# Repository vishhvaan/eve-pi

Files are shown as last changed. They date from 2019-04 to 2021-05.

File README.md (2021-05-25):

The EVoltionary biorEactor

The EVE is an open framework for an automated continuous culture system.

  - Easy to use for programmers and non-programmers
  - Cheap
  - Replicate functionality of a morbidostat/chemostat/turbidostat
  - Versatile & easily modifiable for different purposes

This device is meant to be used for the study of population dynamics and evolution.

# Build it!
Head over to [Start Building] folder to find the 3D stls and circuit schematics (along with KiCAD project). 

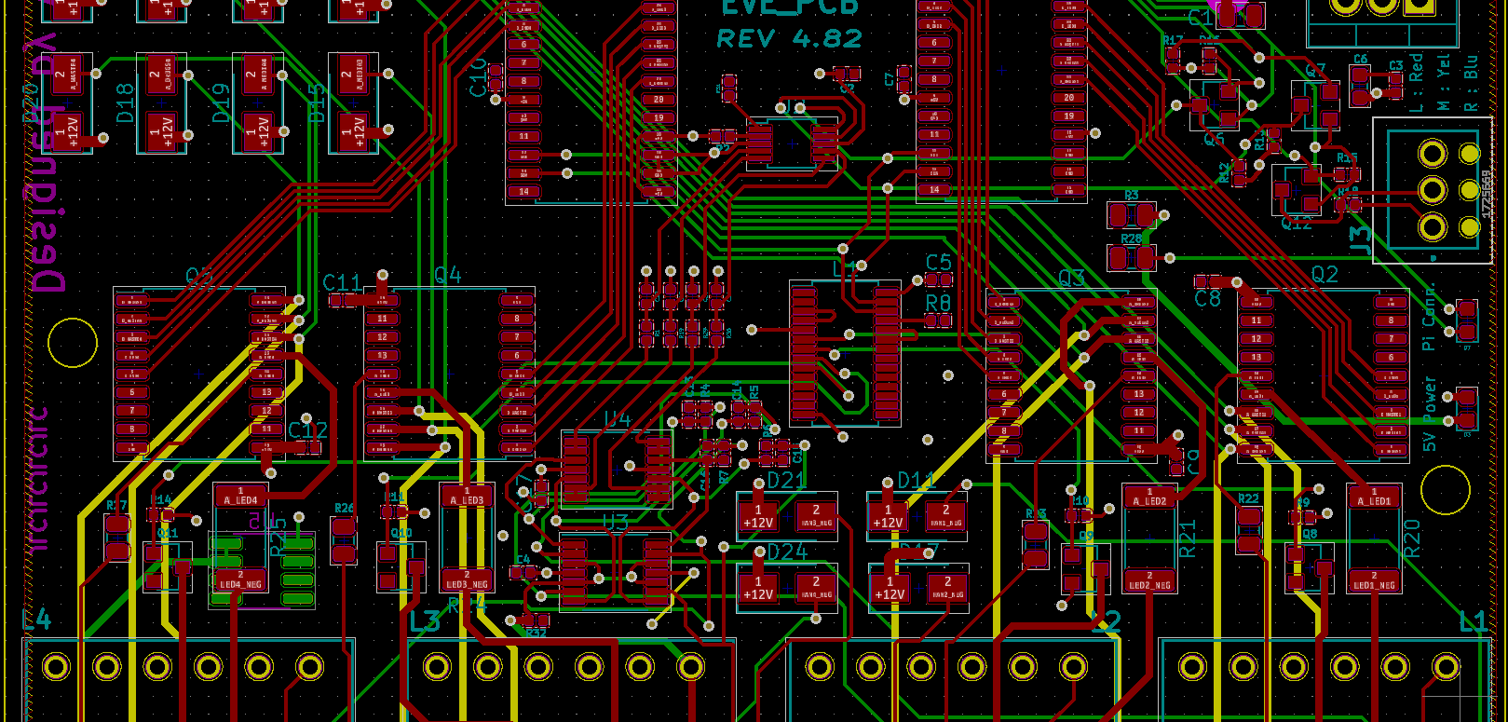
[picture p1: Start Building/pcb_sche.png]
PCB


<p align="center">
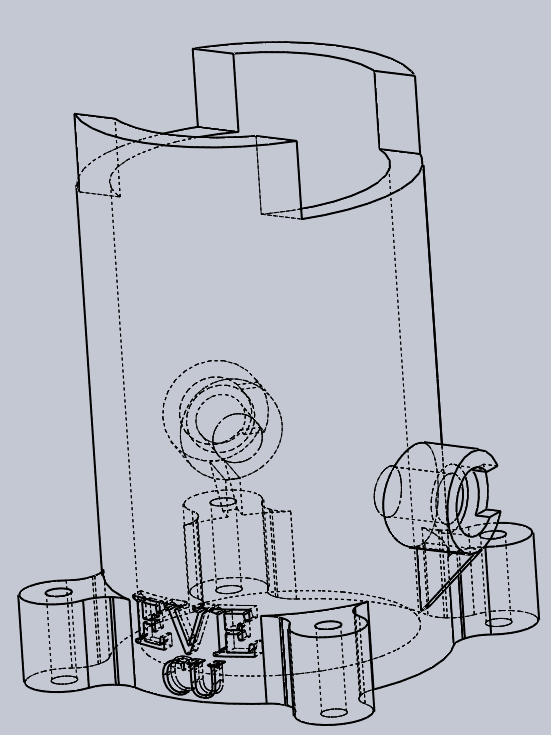
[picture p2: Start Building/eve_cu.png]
  
</p>

# Installation

1. Download and flash the [Raspbian] Buster OS on an SD card.
2. Insert the SD Card into the Pi and connect the Pi to a display, keyboard, local area network, and power.
3. Note the IP address of the device with the command:
```sh
$ ifconfig
```
4. Enter super user mode with the command:
```sh
$ sudo su
```  
5. Run the setup script by entering the command: 
```sh
$ bash <(curl -s https://raw.githubusercontent.com/vishhvaan/eve-pi/master/st_eve.sh)
```
6. Follow the on-screen instructions to install the software.
7. Navigate to the folder `scripts/live/` and copy the `sample-conf.in` to `eve-conf.ini`.
8. Edit the `eve-conf.ini` file based on the "Configuration File Parameter Definitions" file in the "Start Building" folder.\*
9. If the Pi has a browser, navigate to the web interface by accessing: http://localhost.
10. On a browser on the network, navigate to the web interface by accessing the IP address or hostname of the device (e.g. http://eve.local_domain.net).

\* If the PCB is used or the breadboard was wired like the schematic, the default values for the hardware address in the sample-conf.ini file will work.

For a headless install:

1. Download and flash the [Raspbian] Buster OS on an SD card.
2. Add a file titled `ssh` to the boot partition.
3. Insert the SD Card into the Pi and connect the Pi to the local area network and power.
4. In a seperate computer's terminal run a command to connect to the pi.
```sh
$ ssh pi@raspberrypi
```  
5. Login to the pi with the password `raspberry`
6. Continue from step 3 in the non-headless install.

## Install for Docker for ARM Devices
 
Pre-built images coming soon to Docker Hub!

### Build the Docker Image

Use the Dockerfiles in the repo to build images yourself. Use the images to spin up containers in the Pi with EVE WebUI and all the programs built-in.

#### On ARM Devices

1. [Install Docker] on the Raspberry Pi.
2. Install git on the Raspberry Pi.
```sh
$ sudo apt install -y git
```  
2. Clone the repository to the home directory.
```sh
$ sudo git clone https://github.com/vishhvaan/eve-pi.git /eve
```  
3. Move to the correct directory.
```sh
$ cd /eve
``` 
4. Run the Docker build command.
```sh
$ docker build -t eve:pi .
```  
5. Create a container.
```sh
$ docker create --name = eve1 \
    -p 80:80 \
    -p 8050:8050 \
    -e PUID=1000 \
    -e PGID=1000 \
    -v /eve/data:/data \
    eve:pi
```  
6. Start the container.
```sh
$ docker start eve1
```  

#### On UNIX-based x86/x64 Devices
Emulate the ARM environment with QEMU. Build images with the Dockerfile.arm32v7.

### Shout Outs
The EVE uses a number of open source projects to work properly:

  - [script-server] -  Script server to run programs on the Pi
  - [slack-api] - Uses the Slack API for Python for experiment monitoring
  - [plotly] - Uses Dash for real-time plotting
  - [KiCAD] - For Circuit Schematics and PCB Designs
  - [Docker] - For creating self-contained application platforms

## New Features
 
  - Configurable save locations (USB or Network)
  - Combined graphs of culture units

<!--![GitHub All Releases](https://img.shields.io/github/downloads/vishhvaan/eve-pi/total)-->

License
----

MIT

   [script-server]: <https://github.com/bugy/script-server>
   [slack-api]: <https://github.com/slackapi/python-slackclient>
   [Start Building]: <https://github.com/vishhvaan/eve-pi/tree/master/Start%20Building>
   [plotly]: <https://plot.ly/dash/>
   [KiCad]: <http://www.kicad-pcb.org/>
   [Install Docker]: <https://github.com/docker/docker-install>
   [Raspbian]: <https://www.raspberrypi.org/downloads/raspbian/>
   [Docker]: <https://github.com/docker/docker-ce>

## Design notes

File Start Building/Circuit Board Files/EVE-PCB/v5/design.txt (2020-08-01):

3 CU

Daisy Chainable

CU1 = 2 LED/ 2 PD / 4 Pumps
CU1 = 1 LED/ 1 PD / 4 Pumps
CU1 = 1 LED/ 1 PD / 4 Pumps

TCA9548A for sda/scl
- Address select via solder pads
- 8 breakouts

2x PWM PCA9685 
- 16 channels
- 1 x (4pumps, 2LED, 2IND) = 8 channels
- 2 x (4pumps, 1LED, 1IND) = 6 channels
20 channels total

1x ADS1115
- 4 channels
- With op amp for photopdiode

2x AD5241
- 1mohm
- with 1quad opamp
- for inital amp

- op amp with hardwired amp and low pass filter (?)
- amp 5/4
- diode protection for op amp

1x AD5254
- Quad pot
- 10 k
- 5V power + Vab
- CU LED R

1x I2C VRef for OD signals
- Voltage limiting circuit

- high current output voltage follower
- 2x ALM2402-Q1
- (more expensive) 4x OPA564
- 2ohm 1W resistor

Change shotkey to PMEG6010CEH

Logic level inverter for PWM (SN74LVC1G04)
Logic level shifter for SDA/SCL (?)

Integrate Temp Sensor

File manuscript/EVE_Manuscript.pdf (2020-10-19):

Manuscript submitted to eLife
1 | A Low-Cost, Open Source,
2 | Self-Contained Bacterial
3 | EVolutionary biorEactor (EVE)

Vishhvaan Gopalakrishnan¹

, Nikhil P. Krishnan²

, Erin McClure³,†
, Julia Pelesko⁴
4 | ,
Dena Crozier¹,2, Kyle J. Card³

, Drew F.K. Williamson³,‡
, Nathan Webster³
5 | , Daniel
Nichol⁵

, Soumyajit Mandal⁶
, Robert A. Bonomo⁷

, Jacob G. Scott³,4,8,9
6

*For correspondence:
vxg135@case.edu (VG);
scottj10@ccf.org (JGS)

Present address: †University of South Florida Morsani School of Medicine, Tampa, Florida, United States of America; ‡Current Address: Department of Pathology, Brigham and Women’s Hospital, Boston, Massachusetts, United States of America

1
7 | Lerner College of Medicine, Cleveland Clinic, Cleveland, Ohio, United States of America;
| 2
8 | Case Western Reserve University School of Medicine, Cleveland, Ohio, United States of
America; 9
| 3Department of Translational Hematology and Oncology Research, Cleveland
Clinic, Cleveland, Ohio, United States of America; 10
| 4Department of Physics, Case Western
| Reserve University, Cleveland, Ohio, United States of America ; 5
11 | Centre for Evolution
| and Cancer, The Institute of Cancer Research, London, United Kingdom; 6
12 | Integrated
13 | Circuits and Sensor Physics Lab, Case Western Reserve University School of Engineering,
Cleveland, Ohio, United States of America; 14
| 7Department of Medicine, Louis Stokes
15 | Cleveland Department of Veteran Affairs Medical Center, Cleveland, Ohio, United States
of America; 16
| 8Department of Radiation Oncology, Cleveland Clinic, Cleveland, Ohio,
| United States of America; 9
17 | Center for Proteomics and Bioinformatics, Case Western
18 | Reserve University School of Medicine, Cleveland, Ohio, United States of America;
| +
19 | Current Address: University of South Florida Morsani School of Medicine, Tampa,
| Florida, United States of America; 1
20 | Current Address: Department of Pathology, Brigham
21 | and Women’s Hospital, Boston, Massachusetts, United States of America

22

23 | Abstract Evolutionary forces shape bacterial population characteristics in a matter of days.
24 | Here, we present a framework that allows students and scientists to study bacterial evolution of
25 | antibiotic resistance over a few days. This approach is in line with recent efforts to study
26 | evolution of drug resistance in organisms at increasingly smaller time scales and in a
27 | high-throughput manner. One effective approach is through the use of customized bioreactors –
28 | devices that can continuously culture bacteria and monitor population growth in real time. These
29 | devices are often technically challenging and expensive to implement for scientists, let alone
30 | students or teachers who seek an innovative and intuitive way of studying evolution. Here, we
31 | present a continuous bacterial culture device that can be easily and inexpensively constructed,
32 | flexibly configured for various evolution experiments, and used in both academic and
33 | educational environments. As this EVolutionary biorEactor (EVE) is capable of replicating the
34 | functionality of many prominent and expensive bioreactors on the market today, we hope the
35 | greater accessibility of EVE will allow interested high school and college students to study
36 | biological concepts such as population dynamics and evolution using innovative technology.
37 | Within the educational environment, we also hope to foster interaction and interest between the
38 | engineering and biological fields by allowing teachers and students to build their own systems
39 | and share experimental designs and results based on our proposed open framework.

40

41 | Introduction
42 | Continuous microbial culture is a powerful, high-throughput method of observing and directing
43 | evolution in both research and industrial settings. Bioreactors are continuous culture devices that
44 | simultaneously passage media into and remove volume from active cultures to maintain volume
45 | homeostasis Novick and Szilard (1950). The rate of media inflow and outflow is called the dilution
46 | rate; various types of bioreactors dynamically adjust the dilution rate to keep a desired parameter
47 | constant. Chemostats, the simplest bioreactors, maintain a constant dilution rate Voulgarelis et al.
48 | (2019). Turbidostats adjust the dilution rate to maintain a constant turbidity. Finally, auxostats refer
49 | to bioreactors that use any other parameter to control the dilution rate. Examples of parameters
50 | used in auxostats include pH and oxygen tension.
51 | Here, we present a protocol for the assembly and operation of a continuous culture device
52 | called the the EVolutionary biorEactor (EVE). It is a framework for a system which can support mul-
53 | tiple individual bioreactors, which we call culture units (CUs). Each of these CUs are capable of
54 | simultaneously running their own experiment with different antibiotics, rates of passaging media
55 | and removing waste, population density sampling rates, and many other customizable parame-
56 | ters. The EVE system began by openly and cost-conservatively replicating and expanding upon the
57 | morbidostat functionality using the methodology outlined by Toprak et al.. The morbidostat keeps
58 | the cell density low by exposing the population to selective pressures such as cytotoxic drugs. To
59 | prevent extinction of the culture, the morbidostat control algorithm temporally modifies the con-
60 | centration of drug delivered to the in accordance to the adaptive dynamics of the population under
61 | study. Toprak et al. (2013).
62 | The physical functionality of the EVE is centered around a culture vial and is inspired by promi-
63 | nent bioreactors featured in the literature Toprak et al. (2013); Yoshida et al. (2017); Wong et al.
64 | (2018); Milias-Argeitis et al. (2016); Dößelmann et al. (2017). Traditionally, costs of commercially-
65 | available bioreactors range from approximately $10,000 for academic units to $25,000 for the gen-
66 | eral public. These bioreactors are often built specifically for one field of research and are difficult
67 | to modify for other applications. However, a recent shift towards open-source science has brought
68 | about a new wave of do-it-yourself, customized continuous culture devices to accommodate a wide
69 | variety of experimental designs across several research areas Nash (2005); Matteau et al. (2015);
70 | Gill (2018); Cressey (2017); Perkel (2017); Pilizota and Yang (2018). At the same time, the prolif-
71 | eration of maker-spaces throughout high schools and colleges have increased student access to
72 | engineering and design resources. As a result, bioreactors are an ideal educational tool to foster
73 | interest in experimental evolution for college, high school, and even elementary school students.
74 | A few such designs with detailed protocols have already been published in the literature. How-
75 | ever, barriers in electrical, software, and biological expertise, as well as cost, still leave the assembly
76 | and operation of these machines out of reach for students or scientists in resource-poor settings
77 | Yoshida et al. (2017); Toprak et al. (2013); Wong et al. (2018). In addition, increasing the function-
78 | ality of these machines while maintaining cost-effectiveness is an enduring challenge Takahashi
79 | et al. (2014); Liu et al. (2016); Miller et al. (2013); Hoffmann et al. (2017).
80 | Description of the EVE
81 | The primary purpose of the EVE is to record data from sensors that take measurements of growing
82 | cultures. Recorded data fed into programmed logic with the intention of controlling the growth of
83 | the culture over time. Control over the culture is accomplished through the use of pumps which
84 | control the flow of fresh media and drugs into the culture. To do this, a culture is started in a vial and
85 | placed in our custom holder. This holder is positioned on a stand which contains a small fan. The
86 | fan has magnets glued to it so that when the magnets rotate, a magnetic stir-bar at the bottom of
87 | the culture vial is induced to stir. Stirring is useful in two ways: first, to facilitate diffusion of oxygen
88 | into the culture media and second, to keep the culture’s turbidity uniform across the culture vial.
89 | The vial holder also houses two diodes (one LED and one photodiode). Throughout the exper-
90 | iment, the LED shines a light through the culture. Depending on the growth and corresponding

91 | turbidity of the culture, light is variably scattered through the culture, changing the amount of
92 | light that reaches the photodiode (PD). The LED and PD are connected to a circuit board (either a
93 | breadboard or PCB) that powers the devices and converts the analog information from the PD into
94 | digital information. Digital information is recorded by the Raspberry Pi, a single board computer
95 | that controls EVE operation by running the EVE software package. The circuit board is connected
96 | to the Raspberry Pi with a ribbon cable, enabling the two boards to interact digitally. The culture
97 | vial is also connected to three liquid pumps with three plastic tubes. Each pump in turn connects
98 | to either a fresh media reservoir, a media reservoir containing cytotoxic drugs (antibiotics in this
99 | paper), or a waste reservoir. Similar to other bioreactor designs, the culture vials have an air intake
100 | tube that is fitted with an air filter. When powered by the circuit board, a specific pump activates
101 | and pumps either media or media mixed with drug into the vial. The waste pump also activates
102 | whenever the media pumps activate to prevent culture overflow. The waste pump can also provide
103 | the opportunity for easy temporal sampling. The software on the Raspberry Pi is responsible for
104 | triggering these pumps at specific points during the culture to achieve the (user defined) goal of
105 | the experiment. A schematic of the setup is shown in Fig 1.

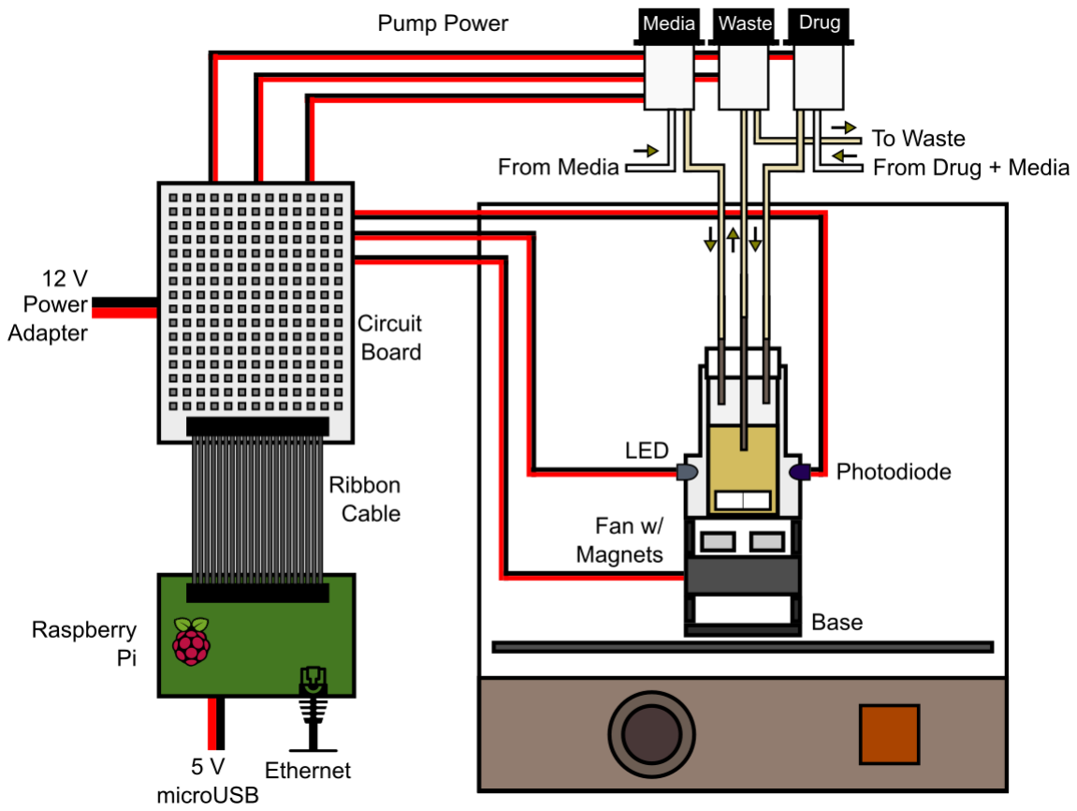
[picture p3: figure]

Figure 1. Hardware schematic of the EVE system. The culture vial is located inside the incubator. As the culture grows, an LED shines a light through the culture. Light that is reflected by the culture is received by the photodiode. A circuit board interprets and conveys photodiode readings to the Pi which runs control software. Based on user-configured directions, and optical density readings, the Pi uses the circuit board to power pumps connected to the vial. This strategy enables precise and dynamic control of the culture.

106 | Before the experiment, the culture vials and reservoirs are sterilized in an autoclave, and the
107 | silicone tubing is sterilized with bleach, ethanol, and sterile water solution, as described in the
108 | supplemental information. The voltage information recorded from the PD reflects the degree to
109 | which light is scattered within the culture vial - a surrogate of the absorbance of the culture. In
110 | many scenarios, the voltage value provides a clear picture of the state of the culture. However, if
111 | a true absorbance is needed, a simple calibration curve correlating the voltage value with an opti-
112 | cal density can be performed. Steps to generate calibration curves, as well as sample calibration
113 | curves are included in the supplemental information.

114 | Overview of Functionality
115 | Prominent bioreactors featured in the literature are quite versatile and can be used to perform
116 | a variety of experiments. The EVE aims to follow suit by being capable of performing a variety of
117 | experiments and is pre-programmed to replicate morbidostat, turbidostat, or chemostat function-
118 | ality. Additional functionality can be programmed for customized needs. To demonstrate the full
119 | functionality of EVE we performed an experiment of bacterial growth under a selective pressure
120 | of ampicillin mixed into media.
121 | Per the morbidostat selection algorithm, drug is introduced to the culture vial as the bacteria
122 | cross a manually set or automatically detected growth threshold. The drug concentration is then
123 | lowered to allow for the recovery of the population to initial population size. This is done by repeti-
124 | tively adding fresh media to the culture while removing waste. In the experimental data below, the
125 | bacterial population is able to recover in 12 hours. The drug solution is then re-introduced to the
126 | culture. After this second introduction, the optical density decreases 15%, indicating development
127 | of tolerance/resistance to the drug. The population is again allowed to recover for a shorter period
128 | – around 6 hours. After this recovery period, the addition of more ampicillin does not kill the pop-
129 | ulation. At the end of the experiment, the cells are effectively resistant to ampicillin. Resistance
130 | of the resultant population can be confirmed with a minimum inhibitory concentration (MIC) as-
131 | say Andrews (2001). The experiment can be performed with a variety of different drugs, however
132 | drug stability in cell culture should be considered. For instance, ampicillin is stable in culture for
133 | 3 days Perlman (1979). If the experiment lasts longer than the stability of the drug in culture, the
134 | drug solution can be refreshed by replacing the drug reservoir with one that is freshly made.
135 | As the experiment progresses, users can monitor the bacteria’s growth via the live web inter-
136 | face or through the included Slack integration. At the end of the experiment, users can parse the
137 | recorded data and visualize the data using their own methods. Graphs of a trial we performed are
138 | included in Fig 2.

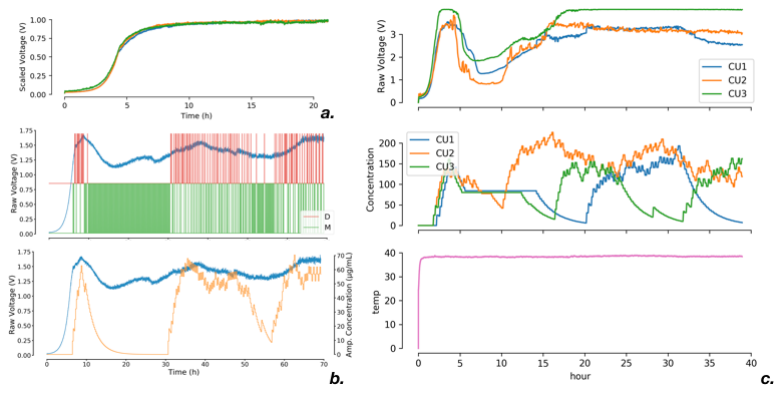
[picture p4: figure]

Figure 2. Experimental data generated from the EVE. (a) Biological replicates (individual CUs) show bacterial growth as voltage measurements. As bacteria grows, more light is scattered on the photodiode and allows precise measurement of growth over time. (b) A single CU grows bacteria (E. coli) into log phase and then introduces the culture to drugs (Ampicilin). The culture is allowed to recover after initial exposure and then is exposed again without allowing ampicilin washout. Slowly, over 72 hours, resistance is evolved in the culture. (c) Even though the same experiment is performed in each of the culture units, each culture behaves differently, allowing users to see the stochasticity of evolution.

139 | Conclusions
140 | We present a low-cost, open-source, extensible, and functionally-flexible bioreactor design. An EVE
141 | build used for simple growth experiments with triplicate CUs can be built for approximately $72,
142 | while an EVE build for directed growth experiments with selective agents will cost approximately
143 | $154.This cost is an estimate for all the parts excluding the incubator, 3D printer costs, and any
144 | glassware needed to prepare the solutions for the experiment. These estimates are included in
145 | the Github repository. []
146 | This is particularly relevant for those who wish to implement the system in the educational
147 | setting. This low cost enables labs to explore concepts of evolution without investing much capital
148 | in tools. A further, novel feature of our system is the ability to manage multiple experimental
149 | protocols at once. The capability of the EVE system to manage multiple protocols in this manner
150 | makes it the only system of its kind that is fully open source and of low-cost.
151 | While current restrictions include limited processing power from the Raspberry Pi, support for
152 | a maximum of 4 simultaneous CUs with the current circuit design, and autonomous passage of
153 | only one drug solution at a time, future modifications can easily be made to the system to address
154 | these limitations. The proposed framework has many applications to the study of evolution for
155 | educational and research purposes as well as directed evolution for industrial applications, and
156 | beyond. Indeed, this device may be used to study a wide variety of biological concepts, even outside
157 | the field of evolutionary biology. The open source nature of the project welcomes modification to
158 | the hardware and the software for more specialized applications of the technology. We hope the
159 | versatile and accessible nature of this device makes it useful for scientists and educators from all
160 | areas.
161 | Materials and Methods
162 | Assembly of the EVE can be separated into hardware and software sections. Hardware setup influ-
163 | ences software configuration, so it is beneficial to start with hardware setup.
164 | Hardware
165 | A list of required hardware components can be found in the GitHub repository. To summarize, the
166 | list of required broad categories of equipment are as follows:
167 | • Incubator
168 | • 3D printed hardware to contain the vial and electronics
169 | • Pumps
170 | • Vials, silicone tubes, and reservoirs
171 | • Circuit board and related electronics
172 | • Raspberry Pi
173 | The GitHub repository contains the following pieces of information in the “Start Building Folder”:
174 | • Circuit schematics and PCB files
175 | • 3D print-able hardware to hold the vials, diodes, caps, magnet-holders, and fans
176 | • Build instructions for experiment equipment
177 | • Experimental procedures
178 | This cost is an estimate for all the parts excluding the incubator, 3D printer costs, and any
179 | glassware needed to prepare the solutions for the experiment.
180 | Circuit board files are packaged in the Github repository and ready to be sent to a PCB manu-
181 | facturer. We used a Chinese manufacture who charged approximately $35 for each PCB. This cost
182 | includes assembly of the PCB with 90% of the surface mounted components as well as shipping
183 | costs.

184 | Software
185 | Software is based on the Python language and can be run from a single Raspberry Pi. Users inter-
186 | act with a simple web interface that is capable of controlling the hardware, running experiments,
187 | and editing configuration files. The web interface used in this project is forked from another open
188 | source script server (https://github.com/bugy/script-server) and modified to integrate with EVE con-
189 | trol applications. This web interface can be utilized by multiple users connected to the local net-
190 | work, allowing for remote monitoring and control of experiments. This network capability of the
191 | device also allows it to save data to network locations, preventing lack of local space on the Pi from
192 | limiting experiment duration. The software allows data to be saved to a USB attached to the Pi or
193 | to network locations mounted to the Pi’s file system. A schematic representation of the software
194 | is in Fig .

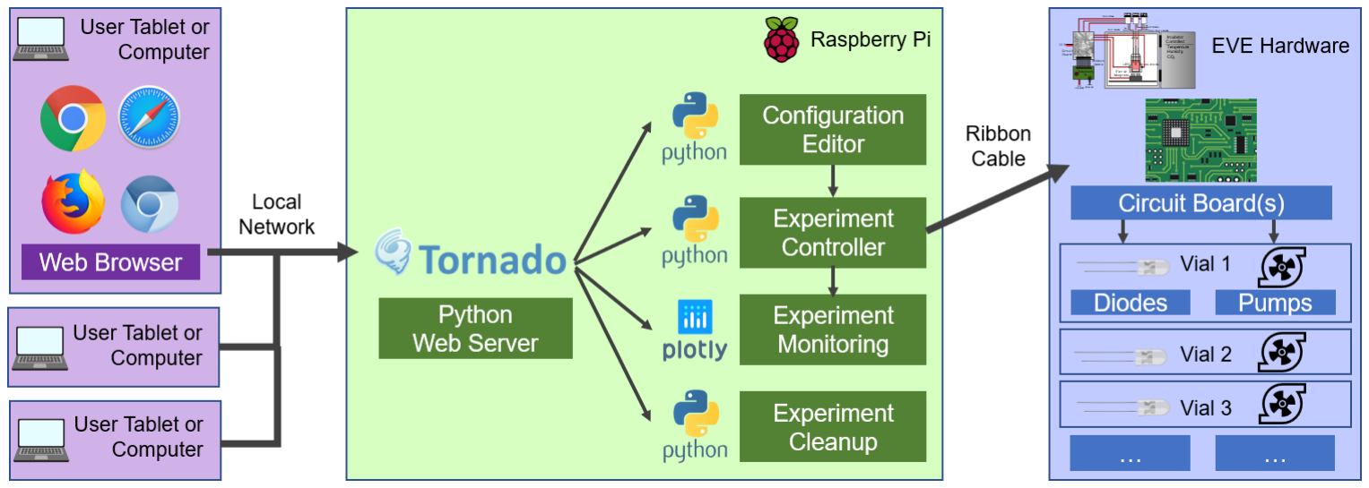
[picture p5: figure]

Figure 3. Software schematic of the EVE system. The device’s software resides on the Raspberry Pi and centers around a Python-based web-server, which serves as the GUI for experimental design and control. The experiment controller application directly interfaces with the circuit board. All of these applications are open source and are built with extensibility in mind.

195 | Further instructions on the setup and use of the software are provided in the Github repository
196 | wiki section. Within the repository, users will be able to download the full software packages and
197 | read about how to use the software. Instructions will also be included along with the software.
198 | There already exists a growing community of users who ask questions within Github and through
199 | email. Some users have modified EVE’s code to work with their projects and are working to con-
200 | tribute code to the base repository. As the user base grows, we expect more code to be made
201 | available and extend the device to specific applications.
202 | Calibration
203 | Calibration can be performed to map voltage of the photodiode (a surrogate of the optical density
204 | of the culture) to the true absorbance of the culture at 600nm. Steps to calibrate the EVE and
205 | sample graphs will be included in the Github repository’s wiki section. The spectrophotometer
206 | that we used to measure the true optical density of the samples was the Biotek Synergy H1 Hybrid
207 | Reader. For the types of LED and photodiodes that we are using, we see a linear relationship
208 | between the voltage and the OD600. Since we are using inexpensive pumps, flow rates should be
209 | measured regularly and updated within the configuration file. By controlling the duration of pump
210 | activation, information bout the flow rates can be used to ensure volume homeostasis.
211 | Supplemental Information
212 | • Github Repository. Contains all the information needed to construct an EVE. All resources
213 | are open-source and under the MIT licence.: https://github.com/vishhvaan/eve-pi
214 | • Start Building Folder. Contains parts list, circuit designs, configuration file definitions, and
215 | printable hardware: https://github.com/vishhvaan/eve-pi/tree/master/Start%20Building

216 | • EVE Wiki. Protocols for biological and experimental setup: https://github.com/vishhvaan/eve-
217 | pi/wiki
218 | Acknowledgments
219 | Rick, our 3D printer. We love you mate. In addition, we’d like to thank VeloSano for their generous
220 | support of this work.
221 | Contributions

222

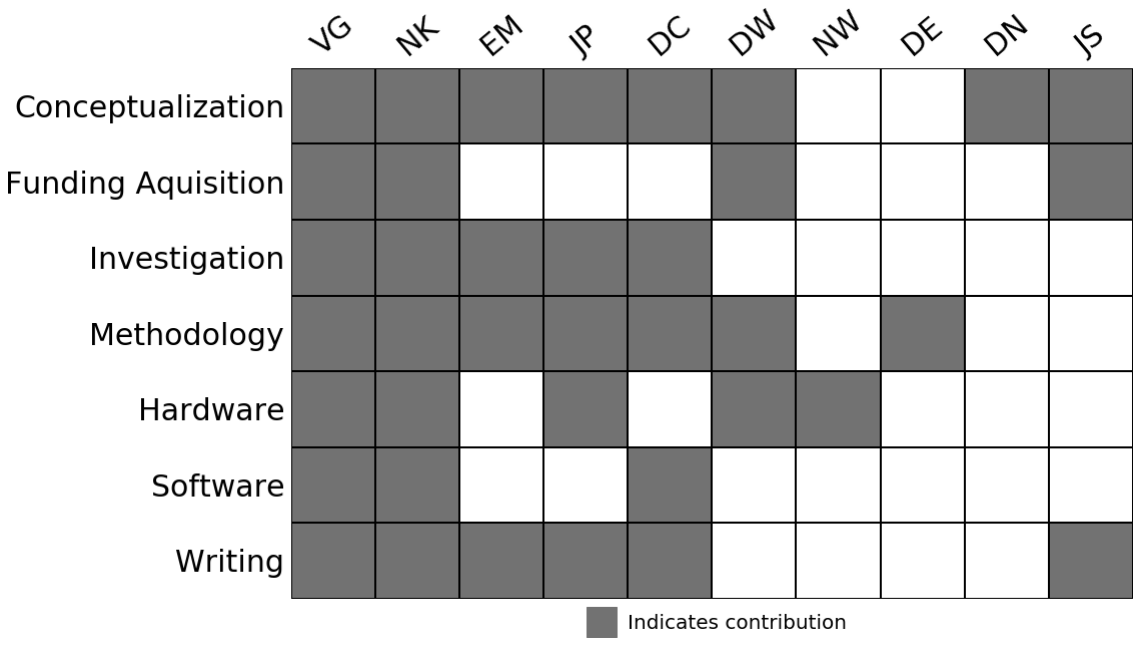
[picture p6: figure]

223 | References
224 | Andrews JM. Determination of minimum inhibitory concentrations. Journal of antimicrobial Chemotherapy.
225 | 2001; 48(suppl_1):5–16.
226 | Cressey D. The DIY electronics transforming research. Nature News. 2017; 544(7648):125.
227 | Dößelmann B, Willmann M, Steglich M, Bunk B, Nübel U, Peter S, Neher RA. Rapid and consistent evolution of
228 | colistin resistance in extensively drug-resistant Pseudomonas aeruginosa during morbidostat culture. An-
229 | timicrobial agents and chemotherapy. 2017; 61(9):e00043–17.
230 | Gill JM, The Internet of Things in the Life Sciences Laboratory. SAGE Publications Sage CA: Los Angeles, CA;
231 | 2018.
232 | Hoffmann SA, Wohltat C, Müller KM, Arndt KM. A user-friendly, low-cost turbidostat with versatile growth rate
233 | estimation based on an extended Kalman filter. PloS one. 2017; 12(7):e0181923.
234 | Liu PC, Lee YT, Wang CY, Yang YT. Design and use of a low cost, automated morbidostat for adaptive evolution
235 | of bacteria under antibiotic drug selection. JoVE (Journal of Visualized Experiments). 2016; (115):e54426.
236 | Matteau D, Baby V, Pelletier S, Rodrigue S. A small-volume, low-cost, and versatile continuous culture device.
237 | PLoS One. 2015; 10(7):e0133384.
238 | Milias-Argeitis A, Rullan M, Aoki SK, Buchmann P, Khammash M. Automated optogenetic feedback control for
239 | precise and robust regulation of gene expression and cell growth. Nature communications. 2016; 7:12546.
240 | Miller AW, Befort C, Kerr EO, Dunham MJ. Design and use of multiplexed chemostat arrays. JoVE (Journal of
241 | Visualized Experiments). 2013; (72):e50262.
242 | Nash DB. Open-Source Science. Biotechnology healthcare. 2005; 2(2):8.
243 | Novick A, Szilard L. Description of the chemostat. Science. 1950; 112(2920):715–716.
244 | Perkel JM. The Internet of Things comes to the lab. Nature News. 2017; 542(7639):125.
245 | Perlman D. [7] Use of antibiotics in cell culture media. In: Methods in enzymology, vol. 58 Elsevier; 1979.p.
246 | 110–116.

247 | Pilizota T, Yang YT. “Do It Yourself” Microbial Cultivation Techniques for Synthetic and Systems Biology: Cheap,
248 | Fun, and Flexible. Frontiers in microbiology. 2018; 9.
249 | Takahashi CN, Miller AW, Ekness F, Dunham MJ, Klavins E. A low cost, customizable turbidostat for use in
250 | synthetic circuit characterization. ACS synthetic biology. 2014; 4(1):32–38.
251 | Toprak E, Veres A, Yildiz S, Pedraza JM, Chait R, Paulsson J, Kishony R. Building a morbidostat: an automated
252 | continuous-culture device for studying bacterial drug resistance under dynamically sustained drug inhibition.
253 | Nature protocols. 2013; 8(3):555.
254 | Voulgarelis D, Velayudhan A, Smith F. Stability of two competing populations in chemostat where one of the
255 | population changes its average mass of division in response to changes of its population. PloS one. 2019;
256 | 14(3):e0213518.
257 | Wong BG, Mancuso CP, Kiriakov S, Bashor CJ, Khalil AS. Precise, automated control of conditions for high-
258 | throughput growth of yeast and bacteria with eVOLVER. Nature biotechnology. 2018; 36(7):614.
259 | Yoshida M, Reyes SG, Tsuda S, Horinouchi T, Furusawa C, Cronin L. Time-programmable drug dosing allows
260 | the manipulation, suppression and reversal of antibiotic drug resistance in vitro. Nature communications.
261 | 2017; 8:15589.

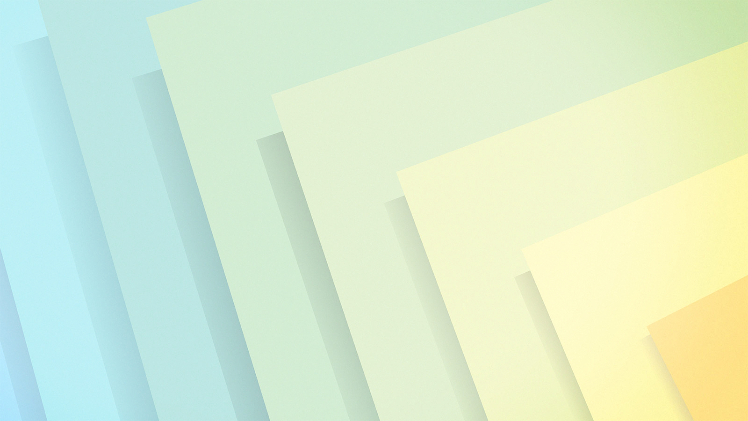
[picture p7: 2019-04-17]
webui/web-src/src/assets/titleBackground.jpg

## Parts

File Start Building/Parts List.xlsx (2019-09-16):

 | Name | Part Number | Unit Price | Quantity Full | Quantity Growth | Part Cost Full | Part Cost Growth | Link
General Hardware
Stir Bars | 20 x 3mm Spin Bars | SBM-2003-MIC | $4.30 | 0.3 | 0.3 | $1.29 | $1.29 | https://www.stirbars.com/list.php?category=Stir%20Bars&subCat=Micro%20PTFE&sessionID=8ad1e715e105bf26aac33fb03c203a40
Large Tubing | 0.125 x 0.250" Tubes | 89068-474 | $130.58 | 0.01 | 0 | $1.31 | $0.00 | https://us.vwr.com/store/product/4640044/vwr-silicone-tubing
Small Tubing | Thermo Scientific Sterilin™ Silicone Tubing | TSR0100050P | $98.83 | 0.06666666667 | 0 | $6.59 | $0.00 | https://www.dynalon.com/PublicStore/product/ESCO-Medical-Grade-Tubing,558,226.aspx
Culture Vials | Fisherbrand™ 20mL Borosilicate Glass Scintillation Vials with White Urea Caps | KFS7451520 | $522.19 | 0.006 | 0.006 | $3.13 | $3.13 | https://www.fishersci.ca/shop/products/fisherbrand-20ml-borosilicate-glass-scintillation-vials-white-urea-caps-3/p-206089
PEEK tubing | PEEK tubing (Fisher Scientific, cat. no. 05-701-6) | UP1538 | $64.89 | 0.15 | 0 | $9.73 | $0.00 | https://www.fishersci.ca/shop/products/upchurch-scientific-peek-tubing-29/057016
Air Filters | Syringe Filters with Acrylic Housing | 28145-477 | $175.84 | 0.06 | 0 | $10.55 | $0.00 | https://us.vwr.com/store/product/4830563/vwr-syringe-filters
Pumps | DC 12V Dosing pump Peristaltic pump dosing Head For Aquarium Lab Analytical Water Micro Tubing Pump |  | $7.69 | 6 | 0 | $46.14 | $0.00 | https://www.aliexpress.com/item/32796657431.html
Male Leur Lock | Cole-Parmer Male Luer with lock ring x 1/16" hose barb, PP, 25/pk | EW-45518-00 | $13.30 | 0.24 | 0 | $3.19 | $0.00 | https://www.coleparmer.com/i/cole-parmer-male-luer-with-lock-ring-x-1-16-hose-barb-pp-25-pk/4551800
Male Leur Thread | Cole-Parmer Male Luer with lock ring x 5/32" hose barb, PP, 25/pk SKU 4551806 | EW-45518-06 | $17.90 | 0.12 | 0 | $2.15 | $0.00 | https://www.coleparmer.com/i/cole-parmer-male-luer-with-lock-ring-x-5-32-hose-barb-pp-25-pk-sku-4551806/4551806
Female Leur | Cole-Parmer Female Luer x 1/4"ID Hose Barb Adapter, Nylon, 25/Pk | EW-45502-20 | $11.80 | 0.36 | 0 | $4.25 | $0.00 | https://www.coleparmer.com/i/cole-parmer-female-luer-x-1-4-id-hose-barb-adapter-nylon-25-pk/4550220
Incubator | Quincy Lab 10-140 Steel/Aluminum/Acrylic Door Analog Incubator, 0.7 Cubic feet, 115V, 120W | Quincy 10-140 | $349.95 | 0 | 0 | $0.00 | $0.00 | https://www.amazon.com/Quincy-10-140-Aluminum-Acrylic-Incubator/dp/B07PHV96K9
Electronics
Micro-computer | RASPBERRY PI 3 MOD B+ BCM2837B0 | RASPBERRY PI 3 MOD B+ BCM2837B0 | $41.56 | 1 | 1 | $41.56 | $41.56 | https://www.digikey.com/product-detail/en/raspberry-pi/RASPBERRY-PI-3-MODEL-B/1690-1025-ND/8571724
LED | EMITTER IR 950NM 150MA RADIAL | TSUS5400 | $0.58 | 3 | 3 | $1.74 | $1.74 | https://www.digikey.com/product-detail/en/vishay-semiconductor-opto-division/TSUS5400/TSUS5400-ND/4073540
Photodiode | SENSOR PHOTODIODE 900NM RADIAL | LTR-323DB | $0.51 | 3 | 3 | $1.53 | $1.53 | https://www.digikey.com/products/en?keywords=160-1987-nd
Fan | 40X40X10 12VDC VAPO 5.4CFM | HA40101V4-1000U-A99 | $4.41 | 3 | 3 | $13.23 | $13.23 | https://www.digikey.com/product-detail/en/sunon-fans/HA40101V4-1000U-A99/259-1790-ND/6198728
ADC | EVAL BOARD ADS1015 12-BIT ADC | ADS1015 | $9.95 | 1 | 1 | $9.95 | $9.95 | https://www.digikey.com/products/en/development-boards-kits-programmers/evaluation-boards-analog-to-digital-converters-adcs/791?k=adafruit%201083
Quad Op Amp | IC OPAMP GP 4 CIRCUIT 14DIP | LM324AN | $0.48 | 1 | 1 | $0.48 | $0.48 | https://www.digikey.com/product-detail/en/texas-instruments/LM324AN/296-9542-5-ND/412056
N-Ch MOSFET | MOSFET N-CH 60V 0.265A SOT-23 | BSN20BKR | $0.06 | 0 | 0 | $0.00 | $0.00 | https://www.digikey.com/product-detail/en/nexperia-usa-inc/BSN20BKR/1727-2341-2-ND/5423827
RPI Breakout | ASSEMBLED PI COBBLER | 2029B | $6.95 | 1 | 1 | $6.95 | $6.95 | https://www.digikey.com/products/en/development-boards-kits-programmers/evaluation-boards-expansion-boards-daughter-cards/797?k=Adafruit%202029
Voltage Regulator | IC REG LINEAR 5V 1.5A TO220-3 | UA7805 | $0.78 | 1 | 1 | $0.78 | $0.78 | https://www.digikey.com/product-detail/en/texas-instruments/UA7805CKCS/296-13996-5-ND/521612
12V Power Supply | AC/DC WALL MOUNT ADAPTER 12V 25W | SWI25-12-N-P5 | $11.62 | 1 | 1 | $11.62 | $11.62 | https://www.digikey.com/product-detail/en/cui-inc/SWI25-12-N-P5/102-4197-ND/7070093
Power Connector | CONN PWR JACK 2X5.5MM SOLDER | PJ-002A | $0.60 | 0 | 0 | $0.00 | $0.00 | https://www.digikey.com/product-detail/en/cui-inc/PJ-002A/CP-002A-ND/96962
Power Circuit Diode | DIODE GEN PURP 800V 1A SMB | S1KB | $0.06 | 0 | 0 | $0.00 | $0.00 | https://www.digikey.com/product-detail/en/diodes-incorporated/S1KB-13-F/S1KB-FDITR-ND/749978
GPIO Extender | IC I/O EXPANDER I2C 16B 28SDIP | MCP23017 | $1.24 | 1 | 1 | $1.24 | $1.24 | https://www.digikey.com/product-detail/en/microchip-technology/MCP23017-E-SP/MCP23017-E-SP-ND/894272
Darlington Transistor Array | TRANS 8NPN DARL 50V 0.5A 18DIP | ULN2803 | $1.19 | 3 | 3 | $3.57 | $3.57 | https://www.digikey.com/product-detail/en/stmicroelectronics/ULN2803A/497-2356-5-ND/599591
Phenonix Terminal Connector | TERM BLK 6POS SIDE ENT 3.5MM PCB | 1841539 | $7.58 | 0 | 0 | $0.00 | $0.00 | https://www.digikey.com/products/en?keywords=1841539
Temperature Sensor | WATERPROOF DS18B20 DIGITAL TEMPE | 381 | $9.95 | 0 | 0 | $0.00 | $0.00 | https://www.digikey.com/product-detail/en/adafruit-industries-llc/381/1528-1592-ND/5875807
Resistors |  |  |  |  |  | $0.00 | $0.00
1 M | RES 1M OHM 1/4W 5% AXIAL | CF14JT1M00 | $0.00475 | 3 | 3 | $0.01 | $0.01 | https://www.digikey.com/product-detail/en/stackpole-electronics-inc/CF14JT1M00/CF14JT1M00TR-ND/1741316
10 k | RES 10K OHM 1/4W 5% AXIAL | CF14JT10K0 | $0.00475 | 3 | 3 | $0.01 | $0.01 | https://www.digikey.com/product-detail/en/stackpole-electronics-inc/CF14JT10K0/CF14JT10K0TR-ND/1741265
400 | RES 400 OHM 0.6W 1% AXIAL | MBB02070C4000FRP00 | $0.03 | 3 | 3 | $0.09 | $0.09 | https://www.digikey.com/product-detail/en/vishay-bc-components/MBB02070C4000FRP00/MBB02070C4000FRP00-ND/5063393
130 | RES 130 OHM 0.6W 1% AXIAL | MRS25000C1300FCT00 | $0.03 | 3 | 3 | $0.09 | $0.09 | https://www.digikey.com/product-detail/en/vishay-bc-components/MRS25000C1300FCT00/BC3985TB-ND/5064051
Capacitors |  |  |  |  |  | $0.00 | $0.00
10 uF | CAP CER 10UF 10V X5R 0805 | CL21A106KPFNNNG | $0.02 | 0 | 0 | $0.00 | $0.00 | https://www.digikey.com/product-detail/en/samsung-electro-mechanics/CL21A106KPFNNNG/1276-6456-2-ND/3894419
0.1 uF | CAP CER 100PF 50V C0G/NP0 0201 | GRM0335C1H101JA01D | $0.0024 | 0 | 0 | $0.00 | $0.00 | https://www.digikey.com/product-detail/en/murata-electronics-north-america/GRM0335C1H101JA01D/490-6113-2-ND/2269165
1 uF | CAP CER 1000PF 50V X7R 0402 | CC0402KRX7R9BB102 | $0.00355 | 0 | 0 | $0.00 | $0.00 | https://www.digikey.com/product-detail/en/yageo/CC0402KRX7R9BB102/311-1036-2-ND/302770
Black Wire | HOOK-UP SOLID 22AWG BLACK 100' | 3051/1 BK005 | $40.50 | 0.06 | 0.03 | $2.43 | $1.21 | https://www.digikey.com/product-detail/en/alpha-wire/3051-1-BK005/A3051B-100-ND/281576
Red Wire | HOOK-UP SOLID 22AWG RED 100' | 3051/1 RD005 | $40.50 | 0.06 | 0.03 | $2.43 | $1.21 | https://www.digikey.com/product-detail/en/alpha-wire/3051-1-RD005/A3051R-100-ND/281577
Schottky Diodes | DIODE SCHOTTKY 30V 200MA DO35 | BAT43 | $0.09 | 9 | 9 | $0.81 | $0.81 | https://www.digikey.com/product-detail/en/stmicroelectronics/BAT43/497-2492-2-ND/603517
Breadboard | BREADBRD TERM STRIP 6.50X2.13" | GS-830 | $8.25 | 2 | 2 | $16.50 | $16.50 | https://www.digikey.com/product-detail/en/global-specialties/GS-830/BKGS-830-ND/5231309
 |  |  |  | Total Cost Full: |  | $203.36
Updated: | 2019-08-08 |  |  |  | Total Cost Growth: |  | $117.02

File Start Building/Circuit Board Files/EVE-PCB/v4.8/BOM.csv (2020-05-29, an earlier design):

Comment | Designator | Footprint | LCSC
10μF | C1 | 805 | C15850
3.9pF | C13,C14,C15,C16 | 402 | C48151
0.1μF | C4,C2,C3,C5,C7,C8,C9,C10,C11,C12 | 402 | C1525
1μF | C6 | 603 | C5673
MUR480ERLG | D1
11-21/BHC-AQ2S1M/2T | D12,D13,D22,D23 | LED_1206 | C264323
19-217/GHC-YR1S2/3T | D3 | LED_0603 | C72043
B160-13-F | D6,D5,D4,D10,D9,D8,D11,D17,D16,D15,D14,D20,D19,D18,D21,D24 | SMA,DO-214AC | C24784
19-213/Y2C-CQ2R2L/3T | D7 | LED_0603 | C72038
PJ-102AH | J1
2x20 Male Header | J2
1725669 | J3
Pheonix 1841539 | L1,L2,L3,L4
UA7805CKCT | Q1 | TO-220-3
ULN2803ADWR | Q2,Q3,Q4,Q5 | SOIC-18_7.5x11.5x1.27P | C9683
DMN10H220L-7 | Q6,Q7,Q12,Q8,Q9,Q10,Q11 | SOT-23-3 | C102615
10KΩ | R13,R17,R2,R12,R16,R8,R9,R10,R11,R14 | 1206 | C25744
4.7kΩ | R15,R18 | 402 | C25900
100Ω | R20,R21,R24,R25 | 2512 | C35218
432Ω | R28,R22,R23,R26,R27 | 805 | C17694
169Ω | R3 | 805 | C17489
1MΩ | R4,R7,R6,R5 | 402 | C26083
PCA9685PW | U1 | TSSOP-28 | C92206
ADS1115IDGSR | U2 | MSOP-10_3.0x3.0x0.5P | C37593
LM324DR | U3 | SOIC-14_3.9x8.7x1.27P | C7943
MCP23017-E/SO | U7,U8 | SOIC-28_300mil | C47023

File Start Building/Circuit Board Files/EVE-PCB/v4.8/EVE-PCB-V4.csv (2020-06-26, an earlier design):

Comment | Designator | Footprint | LCSC
10μF | C1 | 805 | C15850
10pF | C13,C14,C15,C16 | 402 | C32949
0.1μF | C4,C2,C3,C17,C18,C19,C20,C21,C5,C10,C11,C12,C7,C8,C9 | 402 | C1525
1μF | C6 | 603 | C5673
MUR480ERLG | D1 | SMA,DO-214AC
B160-13-F | D16,D15,D14,D20,D19,D18,D21,D24,D6,D5,D4,D10,D9,D8,D11,D17 | SMA,DO-214AC | C24784
11-21/BHC-AQ2S1M/2T | D22,D23,D12,D13 | LED_1206 | C264323
19-217/GHC-YR1S2/3T | D3 | LED_0603 | C72043
19-213/Y2C-CQ2R2L/3T | D7 | LED_0603 | C72038
PJ-102AH | J1
2x20 Male Header | J2
1725669 | J3
Pheonix 1841539 | L3,L4,L1,L2
UA7805CKCT | Q1 | TO-220-3
DMN6140LQ-7 | Q12,Q7,Q6,Q10,Q11,Q8,Q9 | SOT-23-3 | C155271
ULN2803ADWR | Q4,Q5,Q2,Q3 | SOIC-18_7.5x11.5x1.27P | C9683
33KΩ | R1,R19,R29,R30 | 402 | C25779
4.7KΩ | R15,R18 | 402 | C25900
10KΩ | R2,R31,R32,R8,R16,R12,R17,R13,R11,R14,R9,R10 | 402 | C25744
50Ω | R24,R25,R20,R21 | 2512 | C25487
80Ω | R28,R26,R27,R22,R23 | 805 | C17833
169Ω | R3 | 805 | C17489
499KΩ | R4,R7,R6,R5 | 402 | C25793
PCA9685PW | U1 | TSSOP-28 | C92206
ADS1115IDGSR | U2 | MSOP-10_3.0x3.0x0.5P | C37593
TLV4314IPWR | U3,U4 | TSSOP-14 | C106874
MCP1501-10E/SN | U5 | SOIC-8
MCP23017-E/SO | U8,U7 | SOIC-28_300mil | C47023

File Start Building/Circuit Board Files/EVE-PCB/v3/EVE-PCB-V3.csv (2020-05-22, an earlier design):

Comment | Designator | Footprint | LCSC | Package
10μF | C1 | Capacitor_SMD:C_0805_2012Metric | C15850 | 805
470pF | C14,C15,C16,C17 | Capacitor_SMD:C_0402_1005Metric | C92361 | 402
0.1μF | C4,C2,C3,C5,C13,C7,C8,C9,C10,C11,C12 | Capacitor_SMD:C_0402_1005Metric | C1525 | 402
1μF | C6 | Capacitor_SMD:C_0402_1005Metric | C29266 | 402
US1K-13-F | D1 | Diode_SMD:D_SMA | C110532 | SMA,DO-214AC
11-21/BHC-AQ2S1M/2T | D12,D13,D22,D23 | LED_SMD:LED_1206_3216Metric | C264323 | LED_1206
19-217/GHC-YR1S2/3T | D3,D2 | LED_SMD:LED_0603_1608Metric | C72043 | LED_0603
B160-13-F | D6,D5,D4,D10,D9,D8,D16,D15,D14,D20,D19,D18 | Diode_SMD:D_SMA | C24784 | SMA,DO-214AC
19-213/Y2C-CQ2R2L/3T | D7 | LED_SMD:LED_0603_1608Metric | C72038 | LED_0603
PJ-102AH | J1 | Connector_BarrelJack:BarrelJack_CUI_PJ-102AH_Horizontal
2x20 Male Header | J2 | Connector_PinHeader_2.54mm:PinHeader_2x20_P2.54mm_Vertical
Pheonix 1841539 | L1,L2,L3,L4 | SamacSys_Parts:1841539
UA7805CKCT | Q1 | Package_TO_SOT_THT:TO-220-3_Vertical |  | TO-220-3
ULN2803ADWR | Q2,Q3,Q4,Q5 | Package_SO:SOIC-18W_7.5x11.6mm_P1.27mm | C9683 | SOIC-18_7.5x11.5x1.27P
432Ω | R1 | Resistor_SMD:R_1206_3216Metric | C247258 | 1206
14KΩ | R10,R11,R18,R19 | Resistor_SMD:R_0805_2012Metric | C17464 | 805
10KΩ | R13,R17,R2,R12,R16 | Resistor_SMD:R_0402_1005Metric | C25744 | 402
100Ω | R20,R21,R24,R25 | Resistor_SMD:R_2512_6332Metric | C35218 | 2512
432Ω | R28,R22,R23,R26,R27 | Resistor_SMD:R_0805_2012Metric | C17694 | 805
85Ω | R3 | Resistor_SMD:R_0805_2012Metric | C17843 | 805
1MΩ | R4,R7,R6,R5 | Resistor_SMD:R_0402_1005Metric | C26083 | 402
10KΩ | R8,R9,R14,R15 | Resistor_SMD:R_0805_2012Metric | C38522 | 805
AD5254 | U1 | Package_SO:TSSOP-20_4.4x6.5mm_P0.65mm | C207501 | TSSOP-20_4.4x6.5x0.65P
ADS1015IDGSR | U2 | Package_SO:VSSOP-10_3x3mm_P0.5mm | C193969 | VSSOP-10_3.0x3.0x0.5P
LM324DR | U3,U4 | Package_SO:SOIC-14_3.9x8.7mm_P1.27mm | C7943 | SOIC-14_3.9x8.7x1.27P
MMBF170LT1G | U6,U5 | Package_TO_SOT_SMD:SOT-23 | C28871 | SOT-23-3
MCP23017-E/SO | U7,U8 | footprints:SOIC127P1030X265-28N | C47023 | SOIC-28_300mil

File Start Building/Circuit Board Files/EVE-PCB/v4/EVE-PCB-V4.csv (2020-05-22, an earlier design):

Comment | Designator | Footprint | LCSC
10μF | C1 | 805 | C15850
3.9pF | C13,C14,C15,C16 | 402 | C48151
0.1μF | C4,C2,C3,C5,C7,C8,C9,C10,C11,C12 | 402 | C1525
1μF | C6 | 402 | C29266
US1K-13-F | D1 | SMA,DO-214AC | C110532
11-21/BHC-AQ2S1M/2T | D12,D13,D22,D23 | LED_1206 | C264323
19-217/GHC-YR1S2/3T | D3,D2 | LED_0603 | C72043
B160-13-F | D6,D5,D4,D10,D9,D8,D11,D17,D16,D15,D14,D20,D19,D18,D21,D24 | SMA,DO-214AC | C24784
19-213/Y2C-CQ2R2L/3T | D7 | LED_0603 | C72038
PJ-102AH | J1
2x20 Male Header | J2
Pheonix 1841539 | L1,L2,L3,L4
UA7805CKCT | Q1 | TO-220-3
ULN2803ADWR | Q2,Q3,Q4,Q5 | SOIC-18_7.5x11.5x1.27P | C9683
DMN10H220L-7 | Q6,Q7,Q8,Q9,Q10,Q11 | SOT-23-3 | C102615
432Ω | R1 | 1206 | C247258
10KΩ | R13,R17,R2,R12,R16,R8,R9,R10,R11,R14 | 402 | C25744
100Ω | R20,R21,R24,R25 | 2512 | C35218
432Ω | R28,R22,R23,R26,R27 | 805 | C17694
85Ω | R3 | 805 | C17843
1MΩ | R4,R7,R6,R5 | 402 | C26083
PCA9685PW | U1 | TSSOP-28 | C92206
ADS1115IDGSR | U2 | MSOP-10_3.0x3.0x0.5P | C37593
LM324DR | U3 | SOIC-14_3.9x8.7x1.27P | C7943
MCP23017-E/SO | U7,U8 | SOIC-28_300mil | C47023

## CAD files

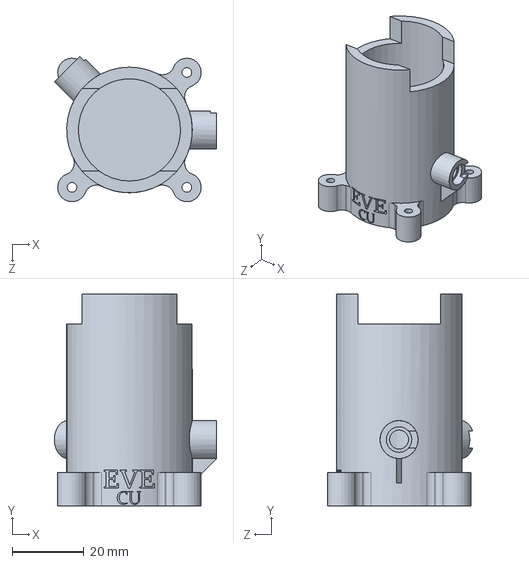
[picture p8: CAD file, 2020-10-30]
Start Building/3D Files/Holder.SLDPRT
45.2 x 59.1 x 40.5 mm

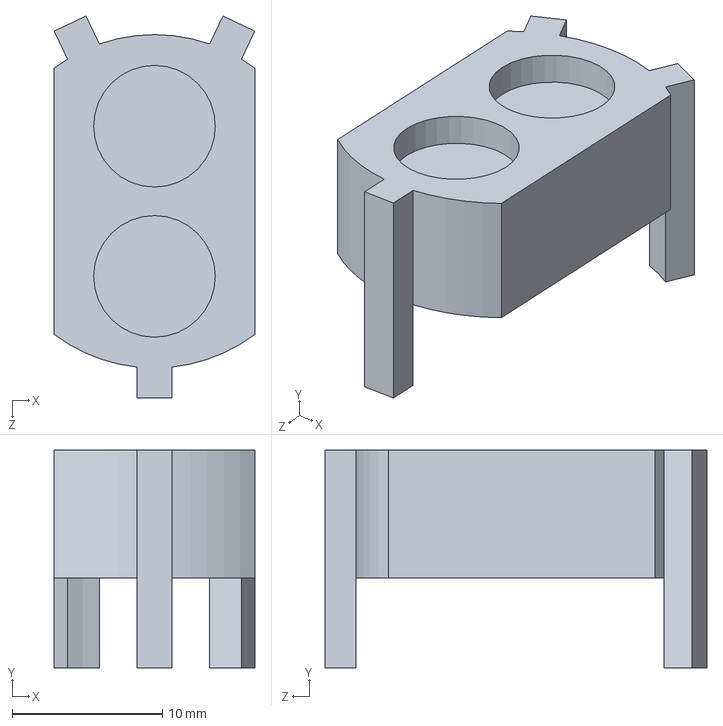
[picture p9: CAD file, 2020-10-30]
Start Building/3D Files/Magnet Holder.SLDPRT
13.4 x 14.5 x 25.4 mm

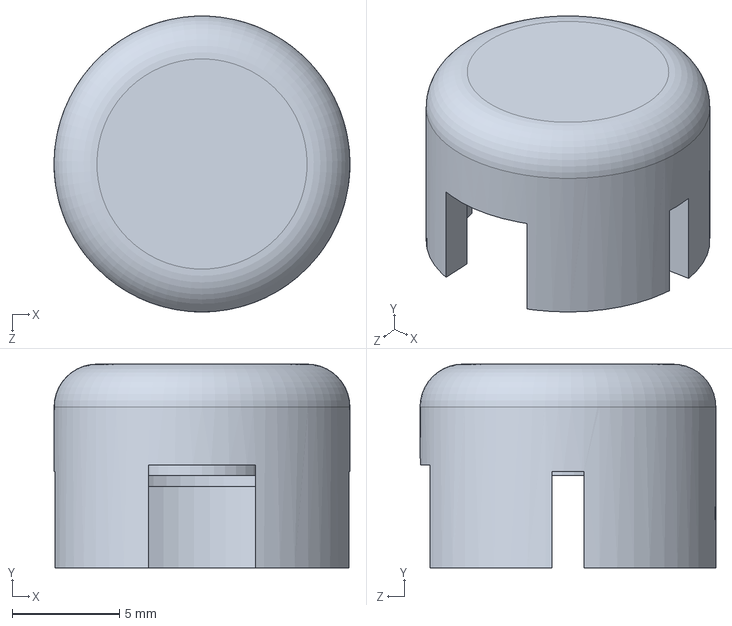
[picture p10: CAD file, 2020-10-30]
Start Building/3D Files/Cap.SLDPRT
13.8 x 9.50 x 13.8 mm

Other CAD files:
Start Building/3D Files/Cap.STL
Start Building/3D Files/Holder.STL
Start Building/3D Files/Magnet Holder.STL

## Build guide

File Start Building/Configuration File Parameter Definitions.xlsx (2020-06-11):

Parameter | Unit | Variable Type | Definition
[MAIN] |  |  | This section contains variables that the master runner uses to coordinate the running of all defined culture units (CUs).
save_location |  |  | File location of the program saves data from experiments. The program will automatically create folders to separate data from different CUs.
repeat1_evar | yes/no |  | If enabled, CUs refer to CU1 for experimental variables. This option is useful when running multiple of the same experiment. Rather than defining the same variables for each CU, only define the variables for CU1 and enable this option. The other CUs will automatically refer to the first CU for experimental variables. Hardware addresses still need to be defined for each CU. This document will classify variables as hardware or experimental.
slack_user |  |  | Username of the bot in Slack.
slack_channel |  |  | Channel where experimental data is uploaded by the bot.
graph_resolution_fac |  |  | This variable decerases the resolution of the real-time graphs to conserve memory resources when the experiment is running. Higher number mean lower resolution.
slack_key |  |  | Slack bot key that enables bot access to the Slack.
multi_icon |  |  | URL of the icon that the multiplexer bot uses when communicating on Slack.
hostname |  |  | Hostname of the Pi. This was define within the setup script.
temp_sensor | yes/no |  | Binary of whether the DS18B20 is connected to the circuit.
comb_graph | yes/no |  | Binary of whether to graph data from all the CUs on the same graph.
comb_graph_freq | Mins |  | Number of mintutes between refreshing the combined graph.
[CU#] |  |  | These sections define the hardware address and the experimental variables of each of the individual culture units.
enabled | yes/no |  | Enable or disable the culture unit. If disabled, all the parameters of the CU will be ignored. No data will be recorded from the CU.
pi_pins | yes/no |  | Whether the pins of the hardware address are pins on the Raspberry Pi's GPIO. "No" indicates that the pins are on the GPIO extender.
a_address |  | hardware address | Decimal I2C address of the ADC converter.
m_address |  | hardware address | Decimal I2C address of the GPIO extender.
pwm_address |  | hardware address | Decimal I2C address of the PWM driver.
p_drug_pins |  | hardware address | Pin that controls the power to the drug pump.
p_nut_pins |  | hardware address | Pin that controls the power to the media pump.
p_waste_pins |  | hardware address | Pin that controls the power to the waste pump.
p_led_pins |  | hardware address | Pin that controls the power to the LED.
p_fan_pins |  | hardware address | Pin that controls the power to the fan.
p_ind_pins |  | hardware address | Pin that controls the optional indicator LED. If there’s no indicator LED, simply leave this option blank.
a_address |  | hardware address | Decimal I2C address of the analog to digital converter.
analogin |  | hardware address | Pin of the analog to digital conveter that is connected to the photodiode.
slack_icon |  |  | URL of the icon that the bot uses when communicating on Slack for the specific CU.
scaling |  | experimental var. | Whether the data should be scaled in real-time based on the maximum detected voltage from the PD. This is useful is there is some variation between the CUs that needs to be normalized.
exp_time_hours | Hours | experimental var. | Experiment duration in hours.
p_drug_times | Seconds | experimental var. | Time that the drug pump runs in seconds.
p_nut_times | Seconds | experimental var. | Time that the media pump runs in seconds.
p_waste_times | Seconds | experimental var. | Time that the waste pump runs in seconds.
drug_pump_flo_rate | mL/sec | experimental var. | Flow rate of the drug pump in mL/sec. This is used to calculate dilution rate of the bioreactor when the drug pump is activated.
nut_pump_flo_rate | mL/sec | experimental var. | Flow rate of the media pump in mL/sec. This is used to calculate dilution rate of the bioreactor when the media pump is activated.
waste_pump_flo_rate | mL/sec | experimental var. | Flow rate of the pump in mL/sec. Used to ensure that the volume entering and exiting the vial is the same.
od_av_length |  | experimental var. | Number of voltage (OD) measurements to average across. This is used to reduce noise in the OD measurements.
time_between_pumps | Mins | experimental var. | Time between intermittent evaluation of the control algorithm and activation of the pumps.
culture_vol | mL | experimental var. | Volume of the culture in mL. Used to calculate drug concentration and dilution rate.
od_thr | V | experimental var. | Voltage at which the system starts pumping drugs.
od_min | V | experimental var. | Voltage at which the system starts pumping media.
time_between_ods | Seconds | experimental var. | Time between intermittent checked of the voltage of the photodioide of this CU.
time_thresh | Mins | experimental var. | Time in minutes between samples of the OD to dynamically set the 'od_thr' variable based on culture growth inside the vial.
od_error | V/hour | experimental var. | Growth rate of the system that is considered high enough to set the 'od_thr' variable and start pumping media.
time_between_graphs |  | experimental var. | Time between generating and uploading real-time graphs to Slack.
time_between_saves |  | experimental var. | Time between saving to data to the save location. The system buffers the data into memory between saves.
drug |  | experimental var. | Name of the drug in the drug reserviour.
drug_conc | μg/mL | experimental var. | Concentration of the drug in the drug reservoir.
selection_alg |  | experimental var. | Selection algorithm that the bioreactor uses. Option include 'morbidostat', 'constant_drug', 'turbidostat', and 'chemostat'
vial_conc | μg/mL | experimental var. | [Only for the 'constant_drug' selection algorithm] Target constant concentration of the drug in the vial. Pumps only activate if the voltage passes the voltage set in the 'od_thr' parameter.

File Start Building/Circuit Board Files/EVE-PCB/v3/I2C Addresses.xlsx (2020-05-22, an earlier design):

Type | Part Number | Bin |  |  |  |  |  |  | Dec
GPIO Extender 1 | MCP23017 | 1 | 0 | 0 | 0 | 0 | 0 | 0 | 64
GPIO Extender 1 | MCP23017 | 1 | 0 | 0 | 0 | 0 | 0 | 1 | 65
ADC | ADS1015 | 1 | 0 | 0 | 1 | 0 | 0 | 0 | 72
DigiPOT | AD5254 | 0 | 1 | 0 | 1 | 1 | 0 | 0 | 44

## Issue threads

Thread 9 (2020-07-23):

### ISSUE TITLE
Where is the photodiode in the schematics?

### ISSUE THREAD

**Issue by CamDavidsonPilon** [vishhvaan/eve-pi#9]
Hi @vishhvaan, I'm quite new to electronics and reading circuit diagrams, so bear with me. I wasn't able to find the photodiode symbol in the schematics.pdf file. Do you mind pointing out where it is?

**Comment by vishhvaan** [comment]
Hi Cam - find the labels PD{x}_NEG and PD{x}_POS where x is the culture unit number. Connect the negative and positive terminals of the photodiode to those labels respectively.

**Comment by CamDavidsonPilon** [comment]
That's what I traced back yea, I guess I was expecting the traditional |◁ symbol, you know? 

Unrelated: How important was using an opamp for this project?

**Comment by vishhvaan** [comment]
You did not find that symbol since the schematics are meant to generate a PCB where we use a terminal block header to connect to the photodiodes.

It is possible to design a circuit without an op amp but most photodiodes circuits use a transimpedance amplifier.

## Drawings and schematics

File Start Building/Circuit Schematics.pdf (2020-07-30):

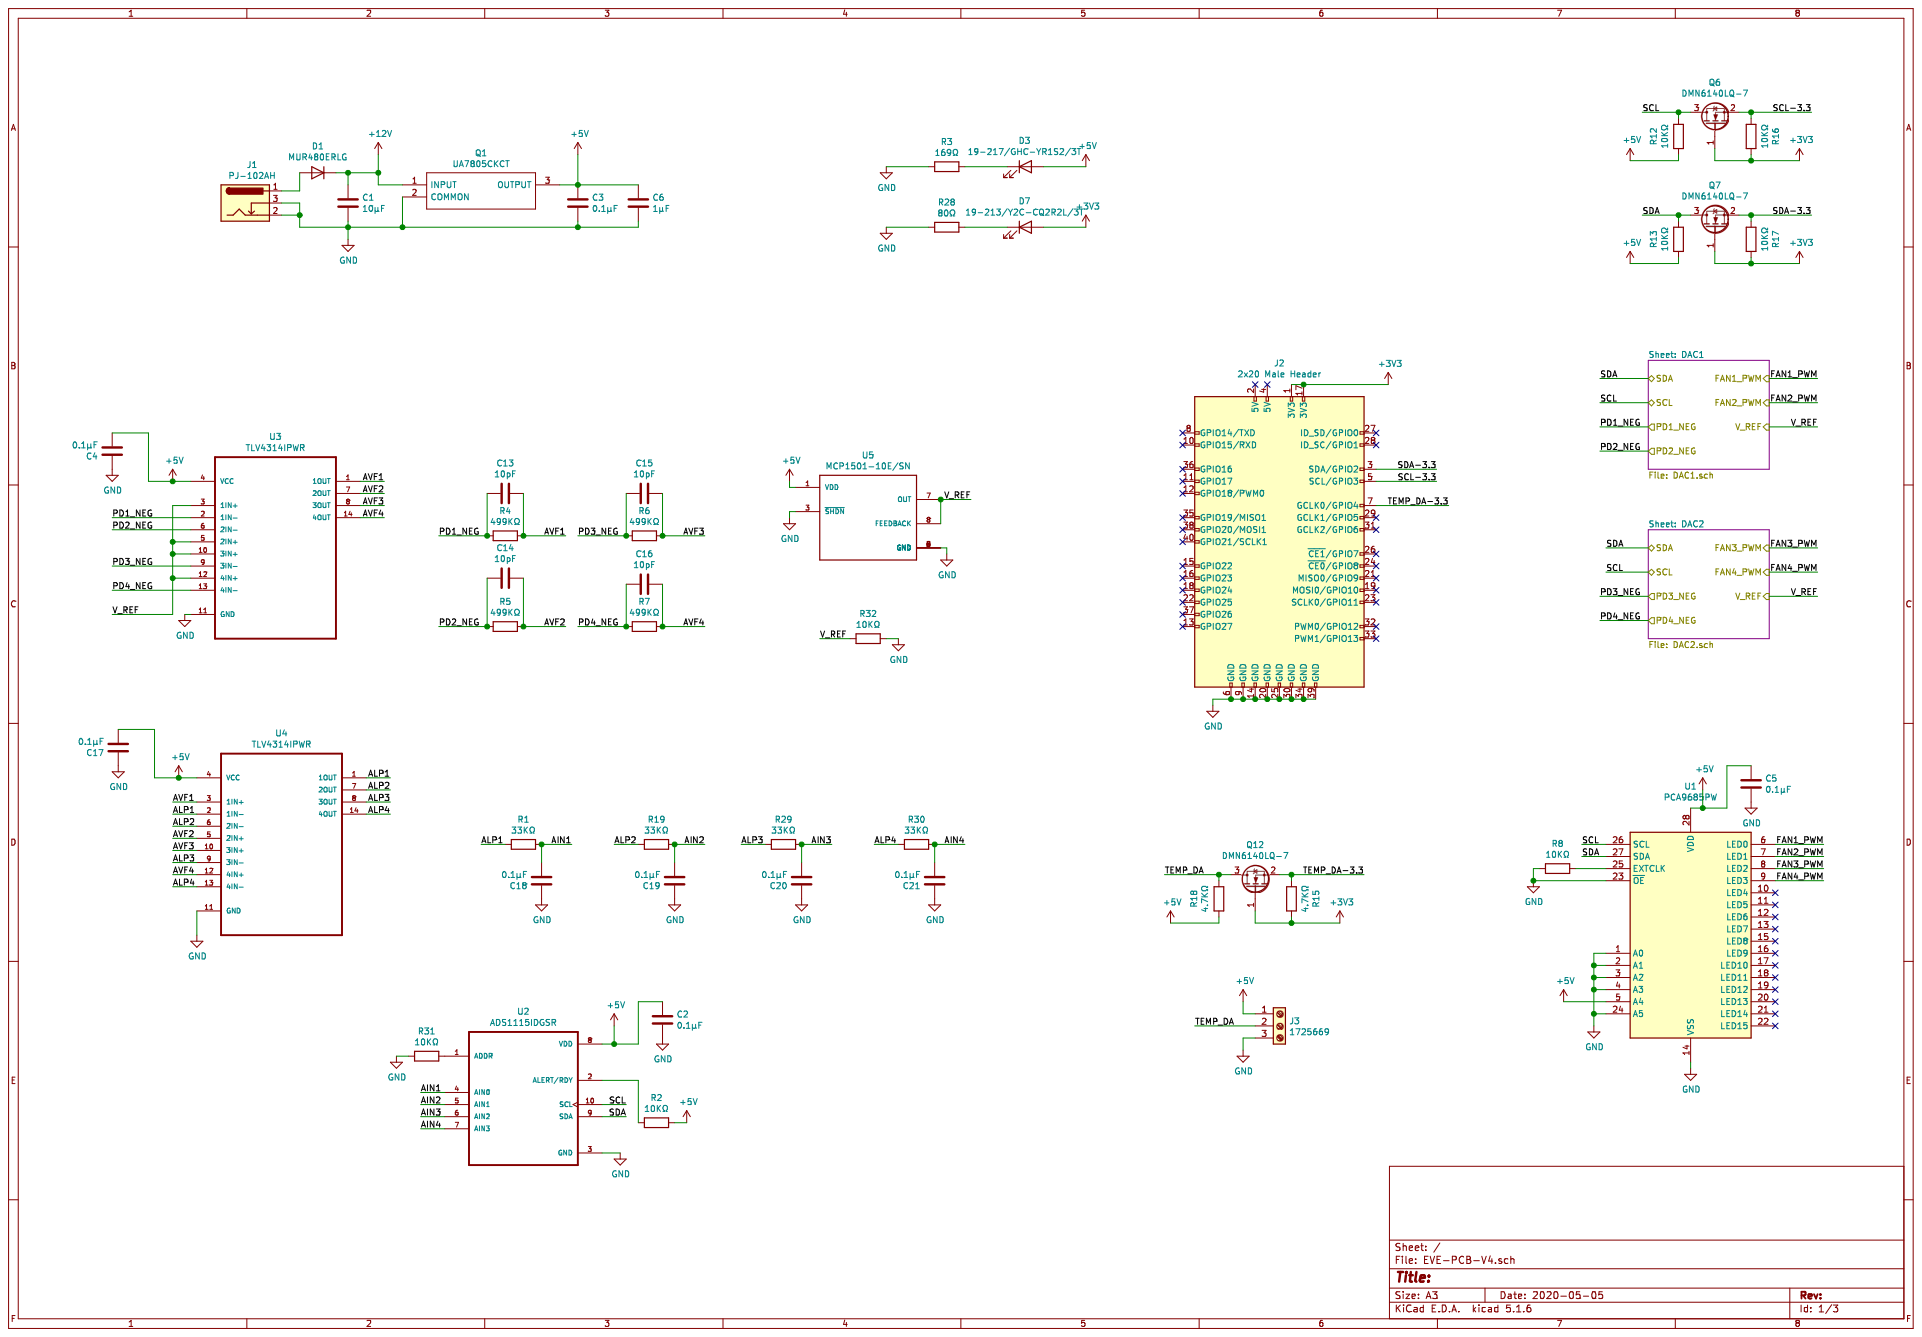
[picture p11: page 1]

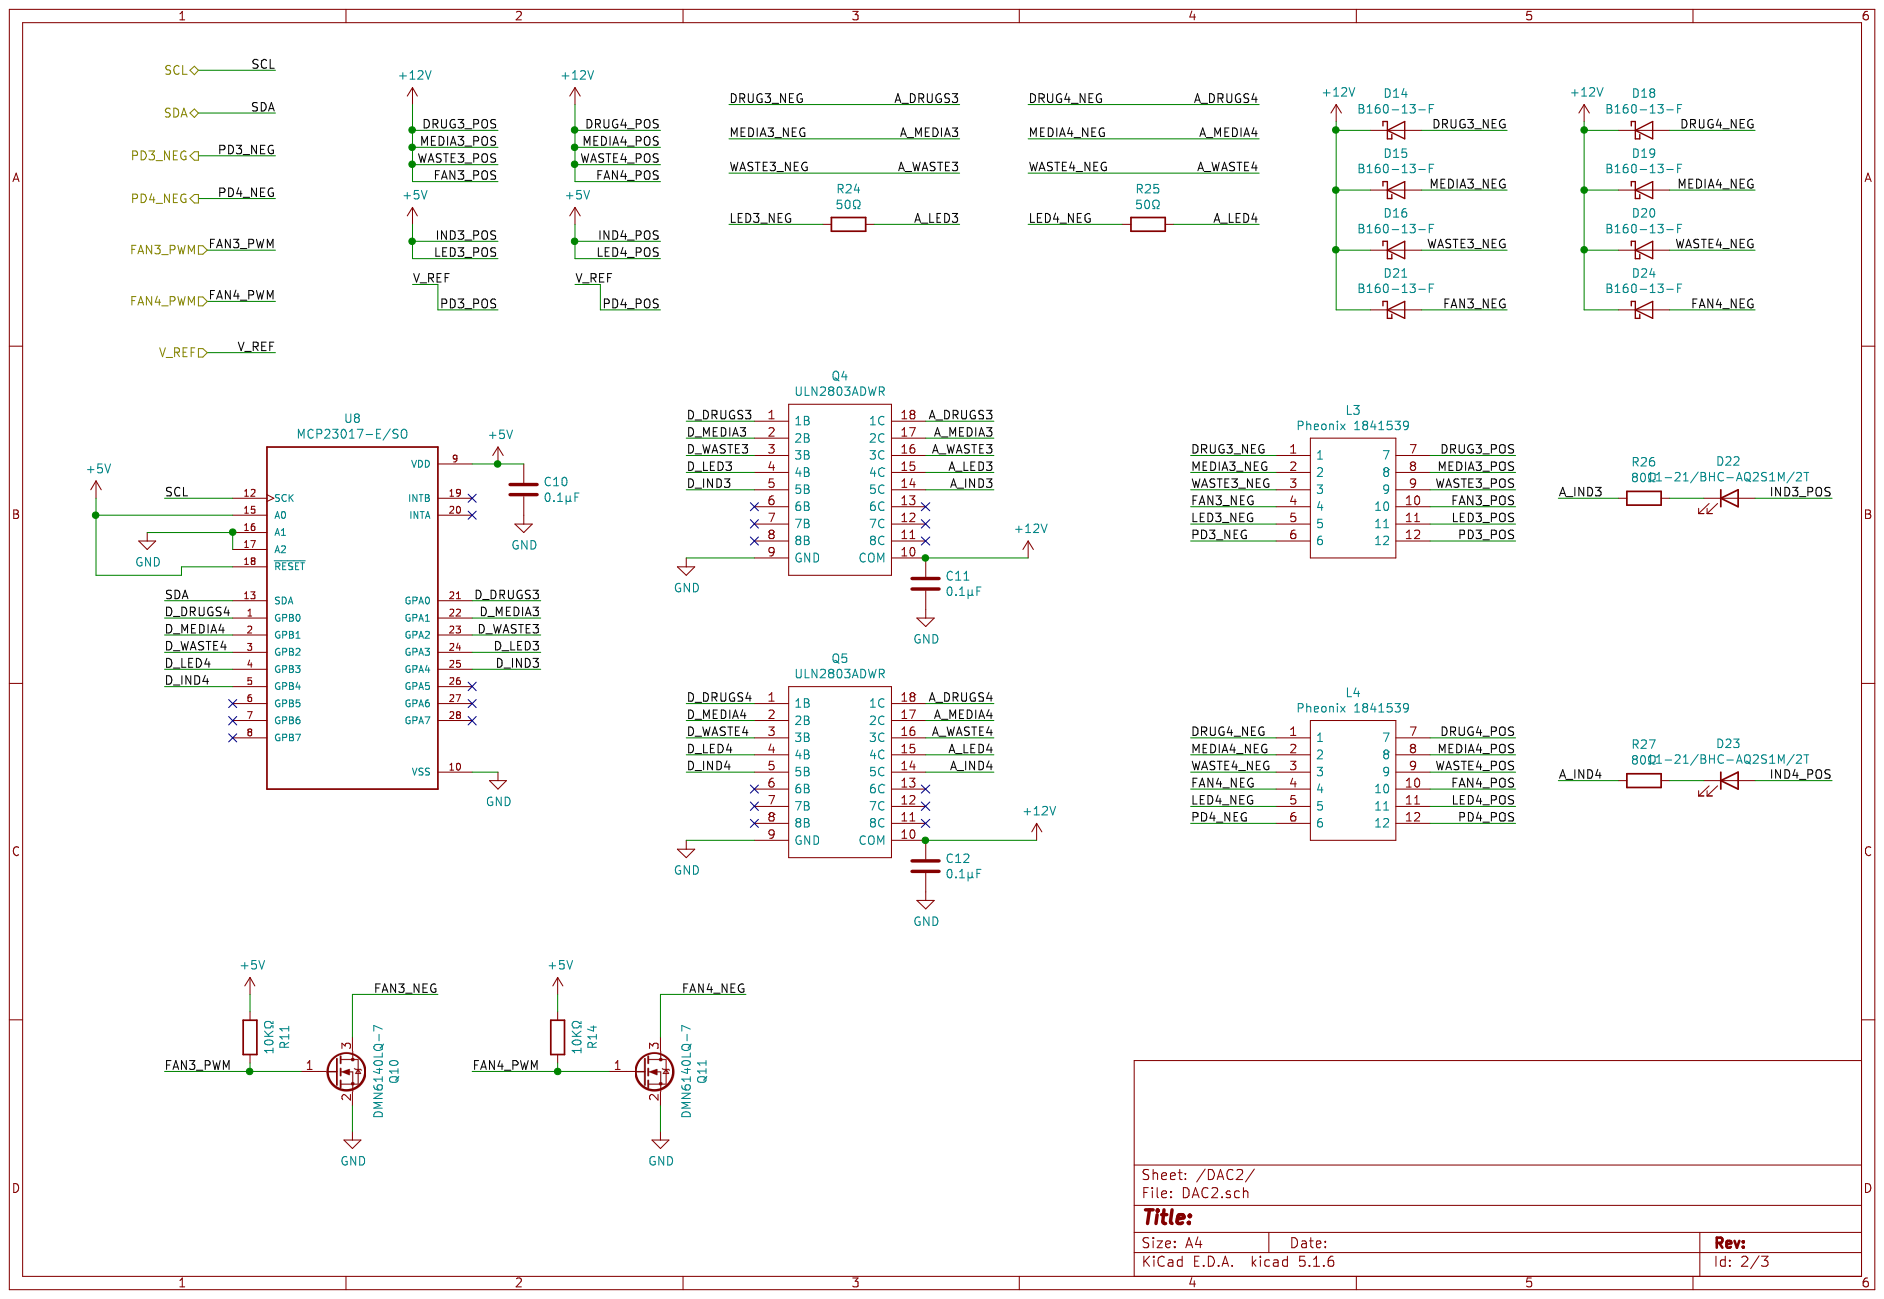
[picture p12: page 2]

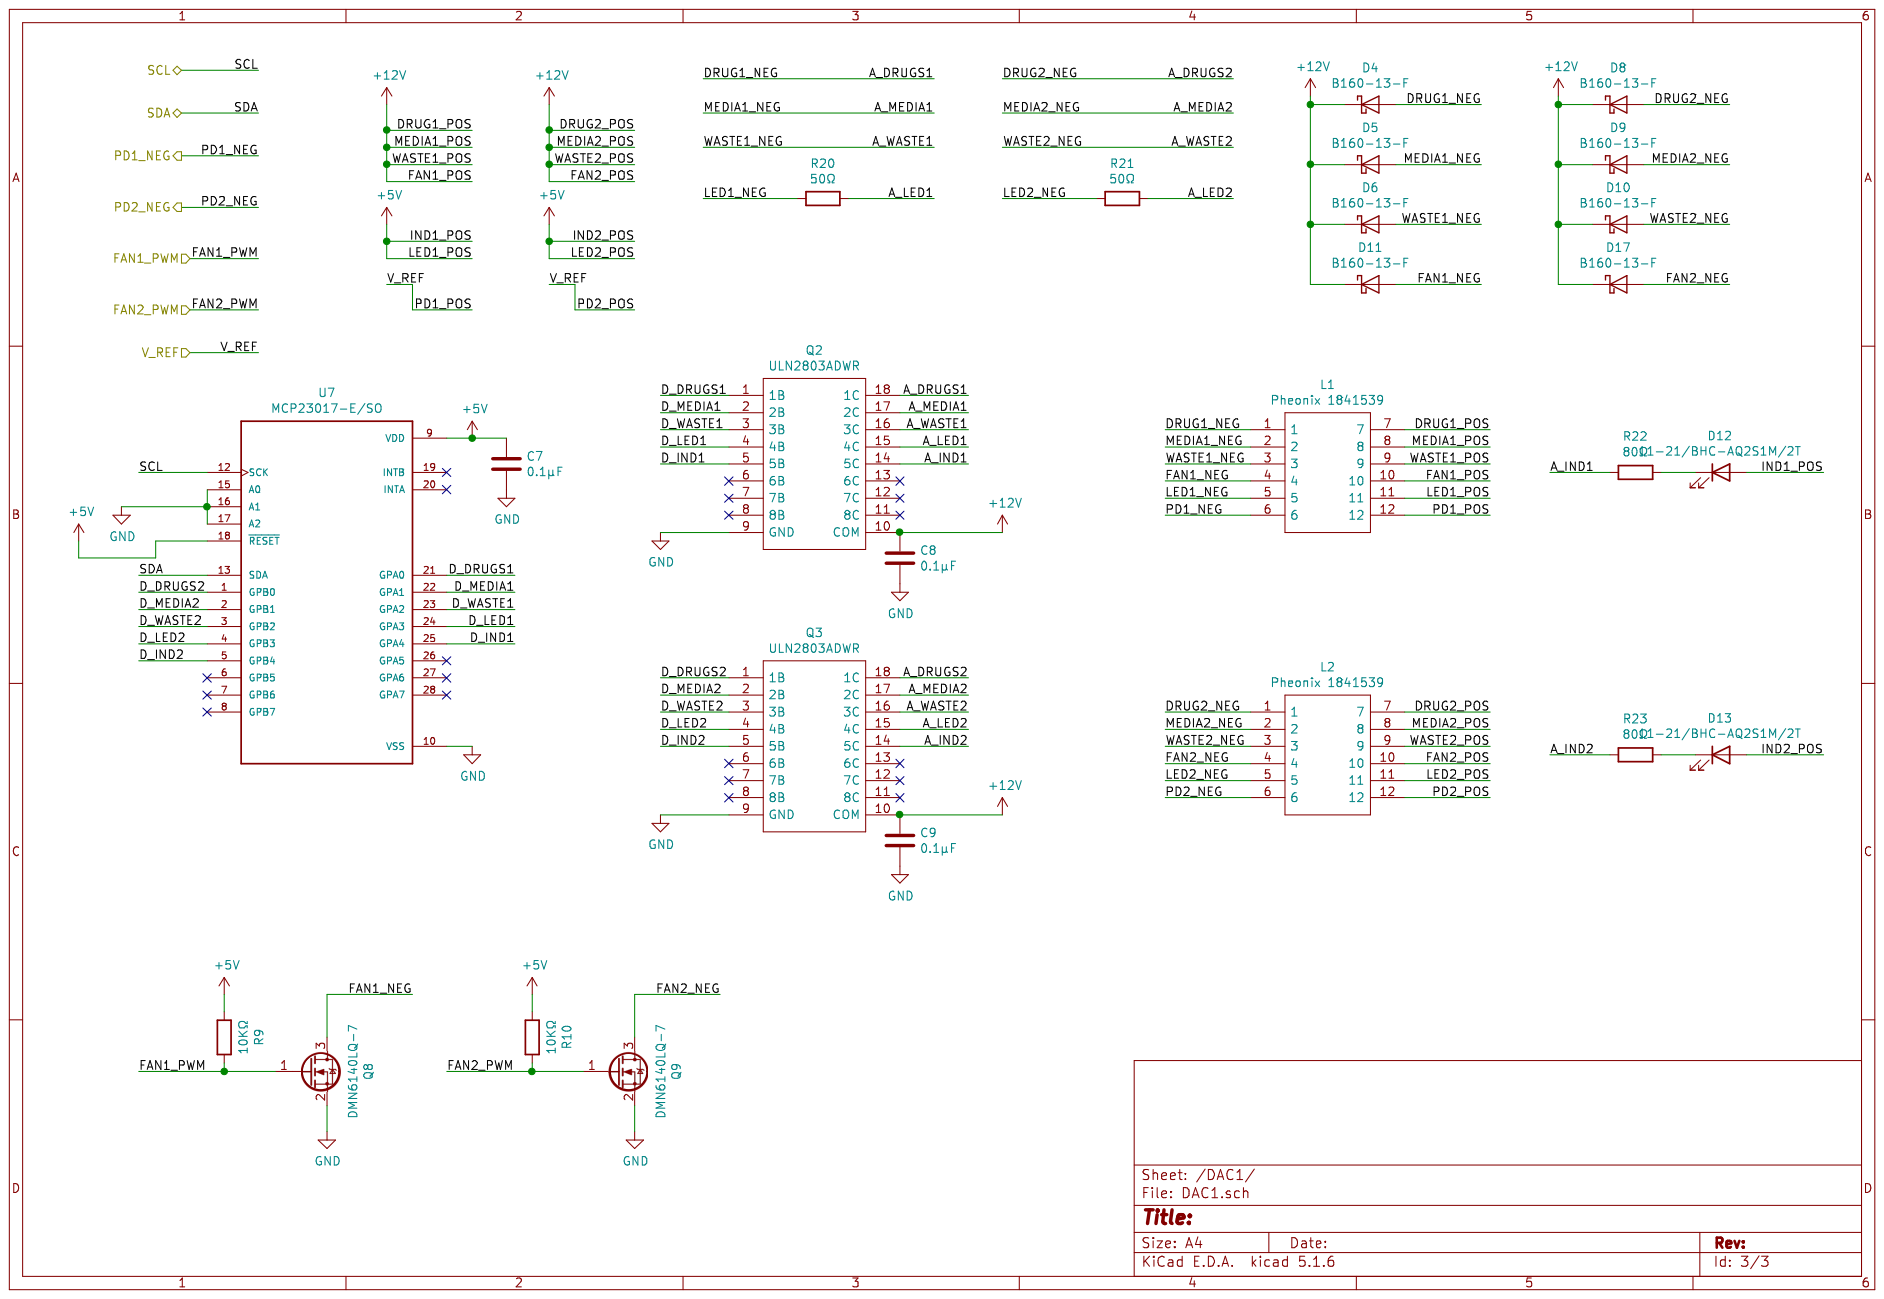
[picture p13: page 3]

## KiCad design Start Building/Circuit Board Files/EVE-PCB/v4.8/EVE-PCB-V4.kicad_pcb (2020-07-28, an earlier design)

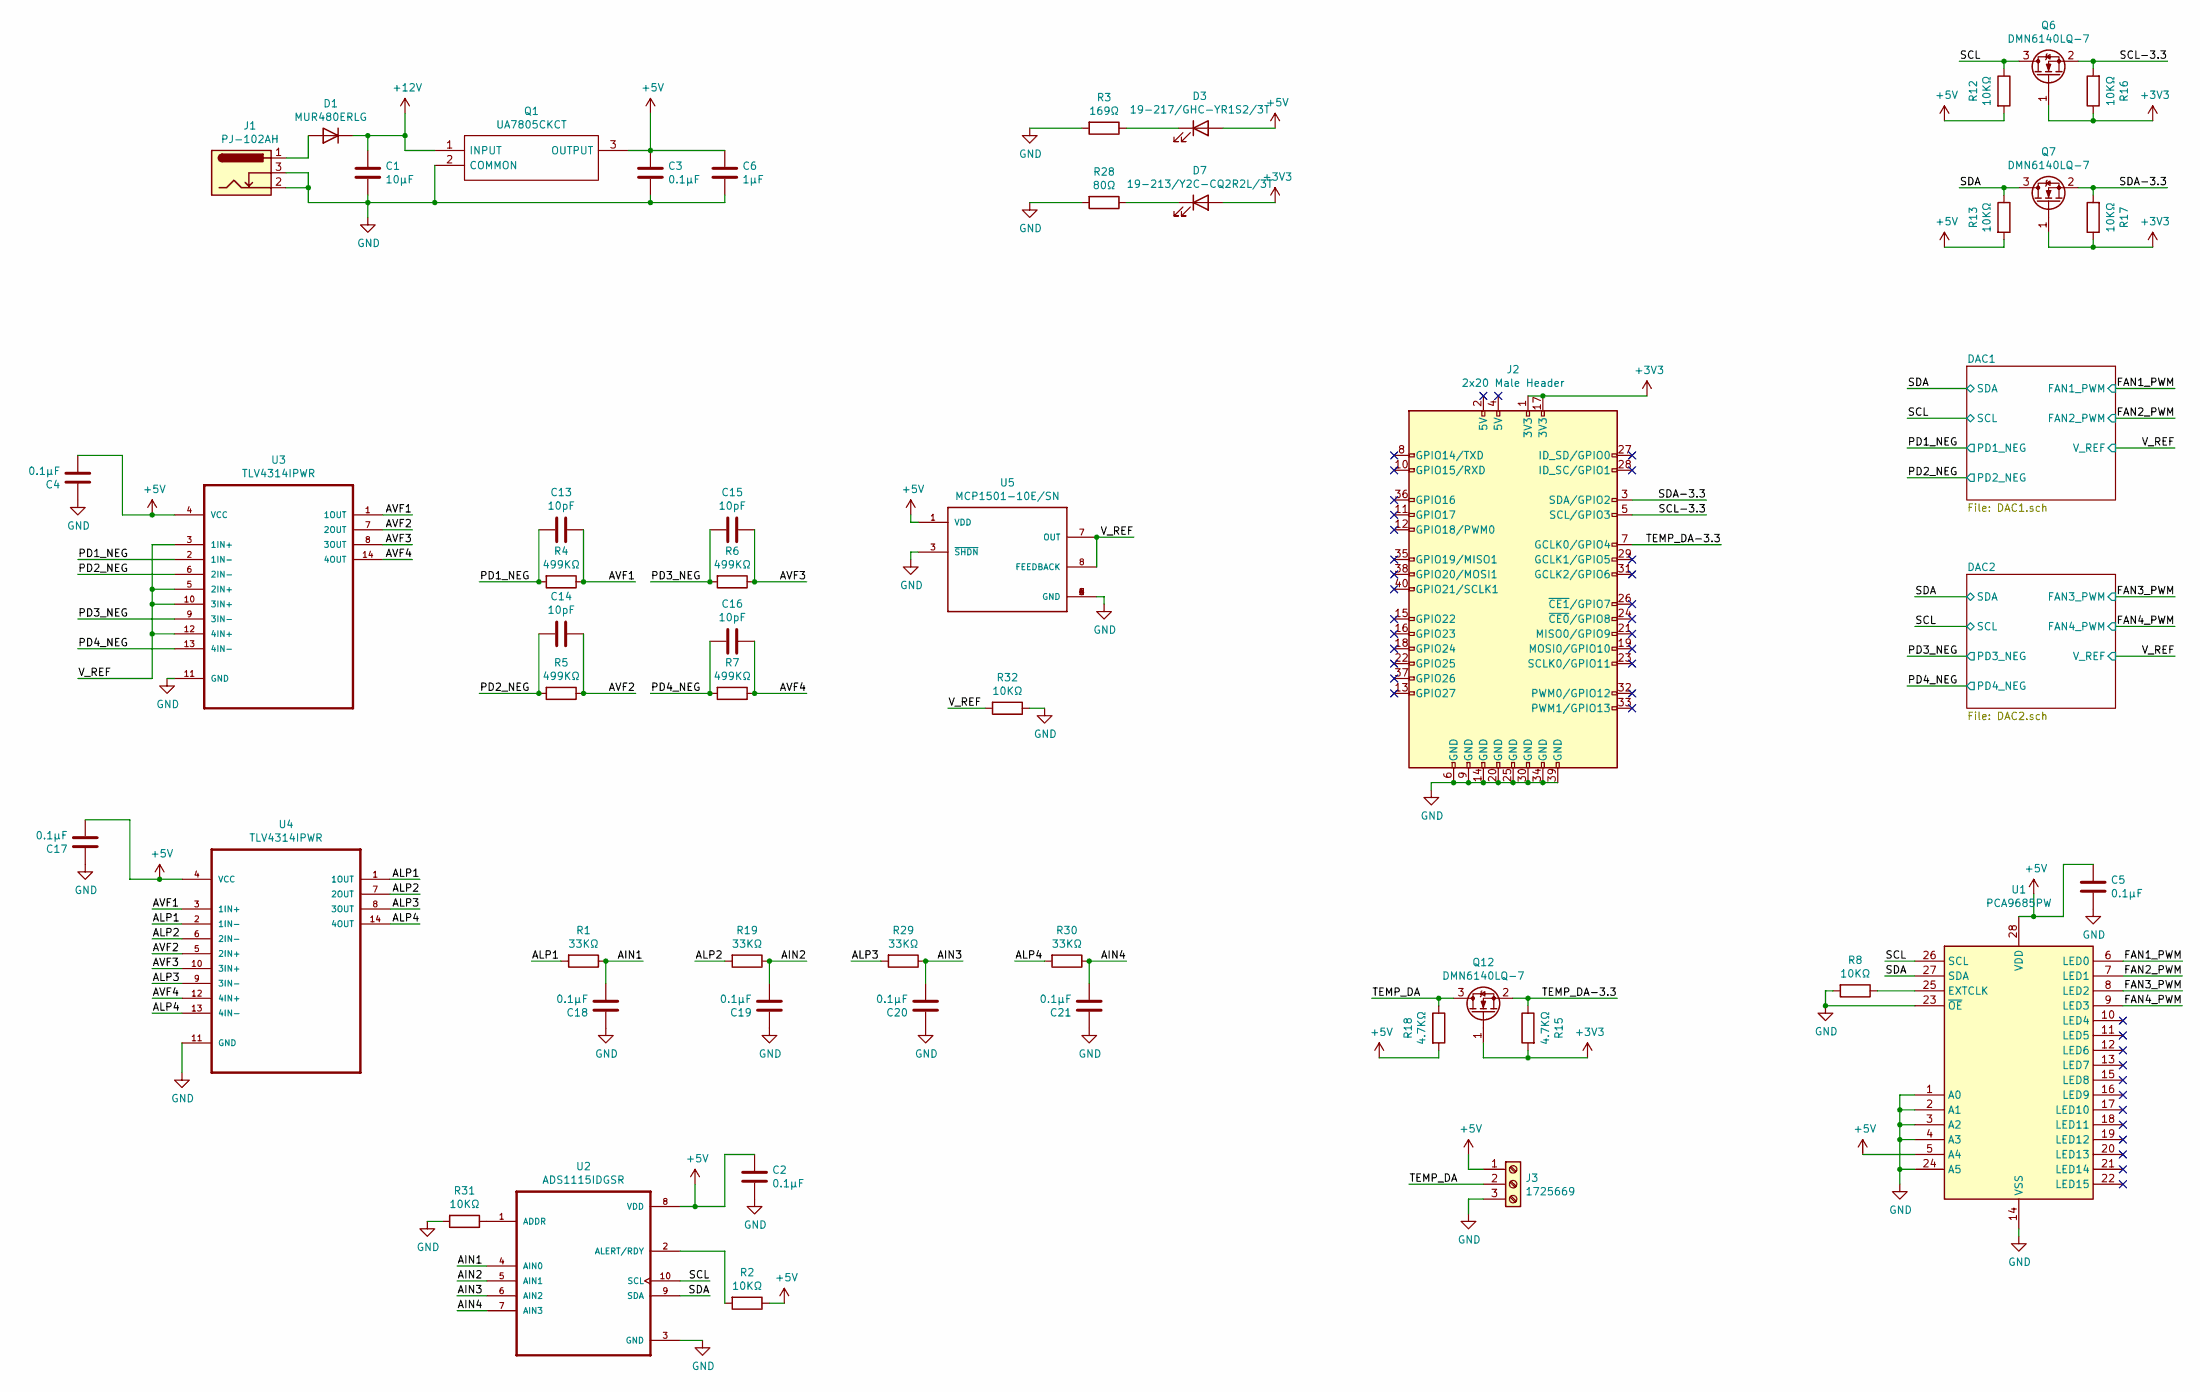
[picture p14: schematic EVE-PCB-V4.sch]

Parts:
C1: 10μF; C_0805_2012Metric; LCSC C15850
C2, C3, C4, C5, C17, C18, C19, C20, C21: 0.1μF; C_0402_1005Metric; LCSC C1525
C6: 1μF; C_0603_1608Metric; LCSC C5673
C13, C14, C15, C16: 10pF; C_0402_1005Metric; LCSC C32949
D1: MUR480ERLG; D_DO-201AE_P3.81mm_Vertical_AnodeUp
D3: 19-217/GHC-YR1S2/3T; LED_0603_1608Metric; LCSC C72043
D7: 19-213/Y2C-CQ2R2L/3T; LED_0603_1608Metric; LCSC C72038
J1: PJ-102AH; BarrelJack_CUI_PJ-102AH_Horizontal
J2: 2x20 Male Header; PinHeader_2x20_P2.54mm_Vertical
J3: 1725669
Q1: UA7805CKCT; TO-220-3_Vertical; Mouser Part Number 595-UA7805CKCT
Q6, Q7, Q12: DMN6140LQ-7; SOT-23; LCSC C155271
R1, R19, R29, R30: 33KΩ; R_0402_1005Metric; LCSC C25779
R2, R8, R12, R13, R16, R17, R31, R32: 10KΩ; R_0402_1005Metric; LCSC C25744
R3: 169Ω; R_0805_2012Metric; LCSC C17489
R4, R5, R6, R7: 499KΩ; R_0402_1005Metric; LCSC C25793
R15, R18: 4.7KΩ; R_0402_1005Metric; LCSC C25900
R28: 80Ω; R_0805_2012Metric; LCSC C17833
U1: PCA9685PW; TSSOP-28_4.4x9.7mm_P0.65mm; LCSC C92206
U2: ADS1115IDGSR; MSOP-10_3x3mm_P0.5mm; LCSC C37593
U3, U4: TLV4314IPWR; TSSOP-14_4.4x5mm_P0.65mm; LCSC C106874
U5: MCP1501-10E/SN; SOIC-8_3.9x4.9mm_P1.27mm

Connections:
+3V3: D7.2 (A), J2.1 (3V3), J2.17 (3V3), Q6.1 (G), Q7.1 (G), Q12.1 (G), R15.2, R16.1, R17.1
+5V: C2.1, C3.1, C4.2, C5.1, C6.1, C17.2, D3.2 (A), J3.1, Q1.3 (OUTPUT), R2.1, R12.2, R13.2, R18.2, U1.5 (A4), U1.28 (VDD), U2.8 (VDD), U3.4 (VCC), U4.4 (VCC), U5.1 (VDD); also elsewhere on the board
+12V: C1.1, D1.1 (K), Q1.1 (INPUT); also elsewhere on the board
/AIN1: C18.2, R1.1, U2.4 (AIN0)
/AIN2: C19.2, R19.1, U2.5 (AIN1)
/AIN3: C20.2, R29.1, U2.6 (AIN2)
/AIN4: C21.2, R30.1, U2.7 (AIN3)
/ALP1: R1.2, U4.1 (1OUT), U4.2 (1IN-)
/ALP2: R19.2, U4.6 (2IN-), U4.7 (2OUT)
/ALP3: R29.2, U4.8 (3OUT), U4.9 (3IN-)
/ALP4: R30.2, U4.13 (4IN-), U4.14 (4OUT)
/AVF1: C13.1, R4.1, U3.1 (1OUT), U4.3 (1IN+)
/AVF2: C14.1, R5.1, U3.7 (2OUT), U4.5 (2IN+)
/AVF3: C15.1, R6.1, U3.8 (3OUT), U4.10 (3IN+)
/AVF4: C16.1, R7.1, U3.14 (4OUT), U4.12 (4IN+)
/FAN1_PWM: U1.6 (LED0); also elsewhere on the board
/FAN2_PWM: U1.7 (LED1); also elsewhere on the board
/FAN3_PWM: U1.8 (LED2); also elsewhere on the board
/FAN4_PWM: U1.9 (LED3); also elsewhere on the board
/PD1_NEG: C13.2, R4.2, U3.2 (1IN-); also elsewhere on the board
/PD2_NEG: C14.2, R5.2, U3.6 (2IN-); also elsewhere on the board
/PD3_NEG: C15.2, R6.2, U3.9 (3IN-); also elsewhere on the board
/PD4_NEG: C16.2, R7.2, U3.13 (4IN-); also elsewhere on the board
/SCL: Q6.3 (D), R12.1, U1.26 (SCL), U2.10 (SCL); also elsewhere on the board
/SCL-3.3: J2.5 (SCL/GPIO3), Q6.2 (S), R16.2
/SDA: Q7.3 (D), R13.1, U1.27 (SDA), U2.9 (SDA); also elsewhere on the board
/SDA-3.3: J2.3 (SDA/GPIO2), Q7.2 (S), R17.2
/TEMP_DA: J3.2, Q12.3 (D), R18.1
/TEMP_DA-3.3: J2.7 (GCLK0/GPIO4), Q12.2 (S), R15.1
/V_REF: R32.2, U3.3 (1IN+), U3.5 (2IN+), U3.10 (3IN+), U3.12 (4IN+), U5.7 (OUT), U5.8 (FEEDBACK); also elsewhere on the board
GND: C1.2, C2.2, C3.2, C4.1, C5.2, C6.2, C17.1, C18.1, C19.1, C20.1, C21.1, J1.2, J1.3, J2.6 (GND), J2.9 (GND), J2.14 (GND), J2.20 (GND), J2.25 (GND), J2.30 (GND), J2.34 (GND), J2.39 (GND), J3.3, Q1.2 (COMMON), R3.2, R8.2, R28.2, R31.2, R32.1, U1.1 (A0), U1.2 (A1), U1.3 (A2), U1.4 (A3), U1.14 (VSS), U1.23 (~OE), U1.24 (A5), U2.3 (GND), U3.11 (GND), U4.11 (GND), U5.2 (GND), U5.3 (~SHDN~), U5.4 (GND), U5.5 (GND), U5.6 (GND); also elsewhere on the board
unnamed: D1.2 (A), J1.1
unnamed: D3.1 (K), R3.1
unnamed: D7.1 (K), R28.1
unnamed: R2.2, U2.2 (ALERT/RDY)
unnamed: R8.1, U1.25 (EXTCLK)
unnamed: R31.1, U2.1 (ADDR)

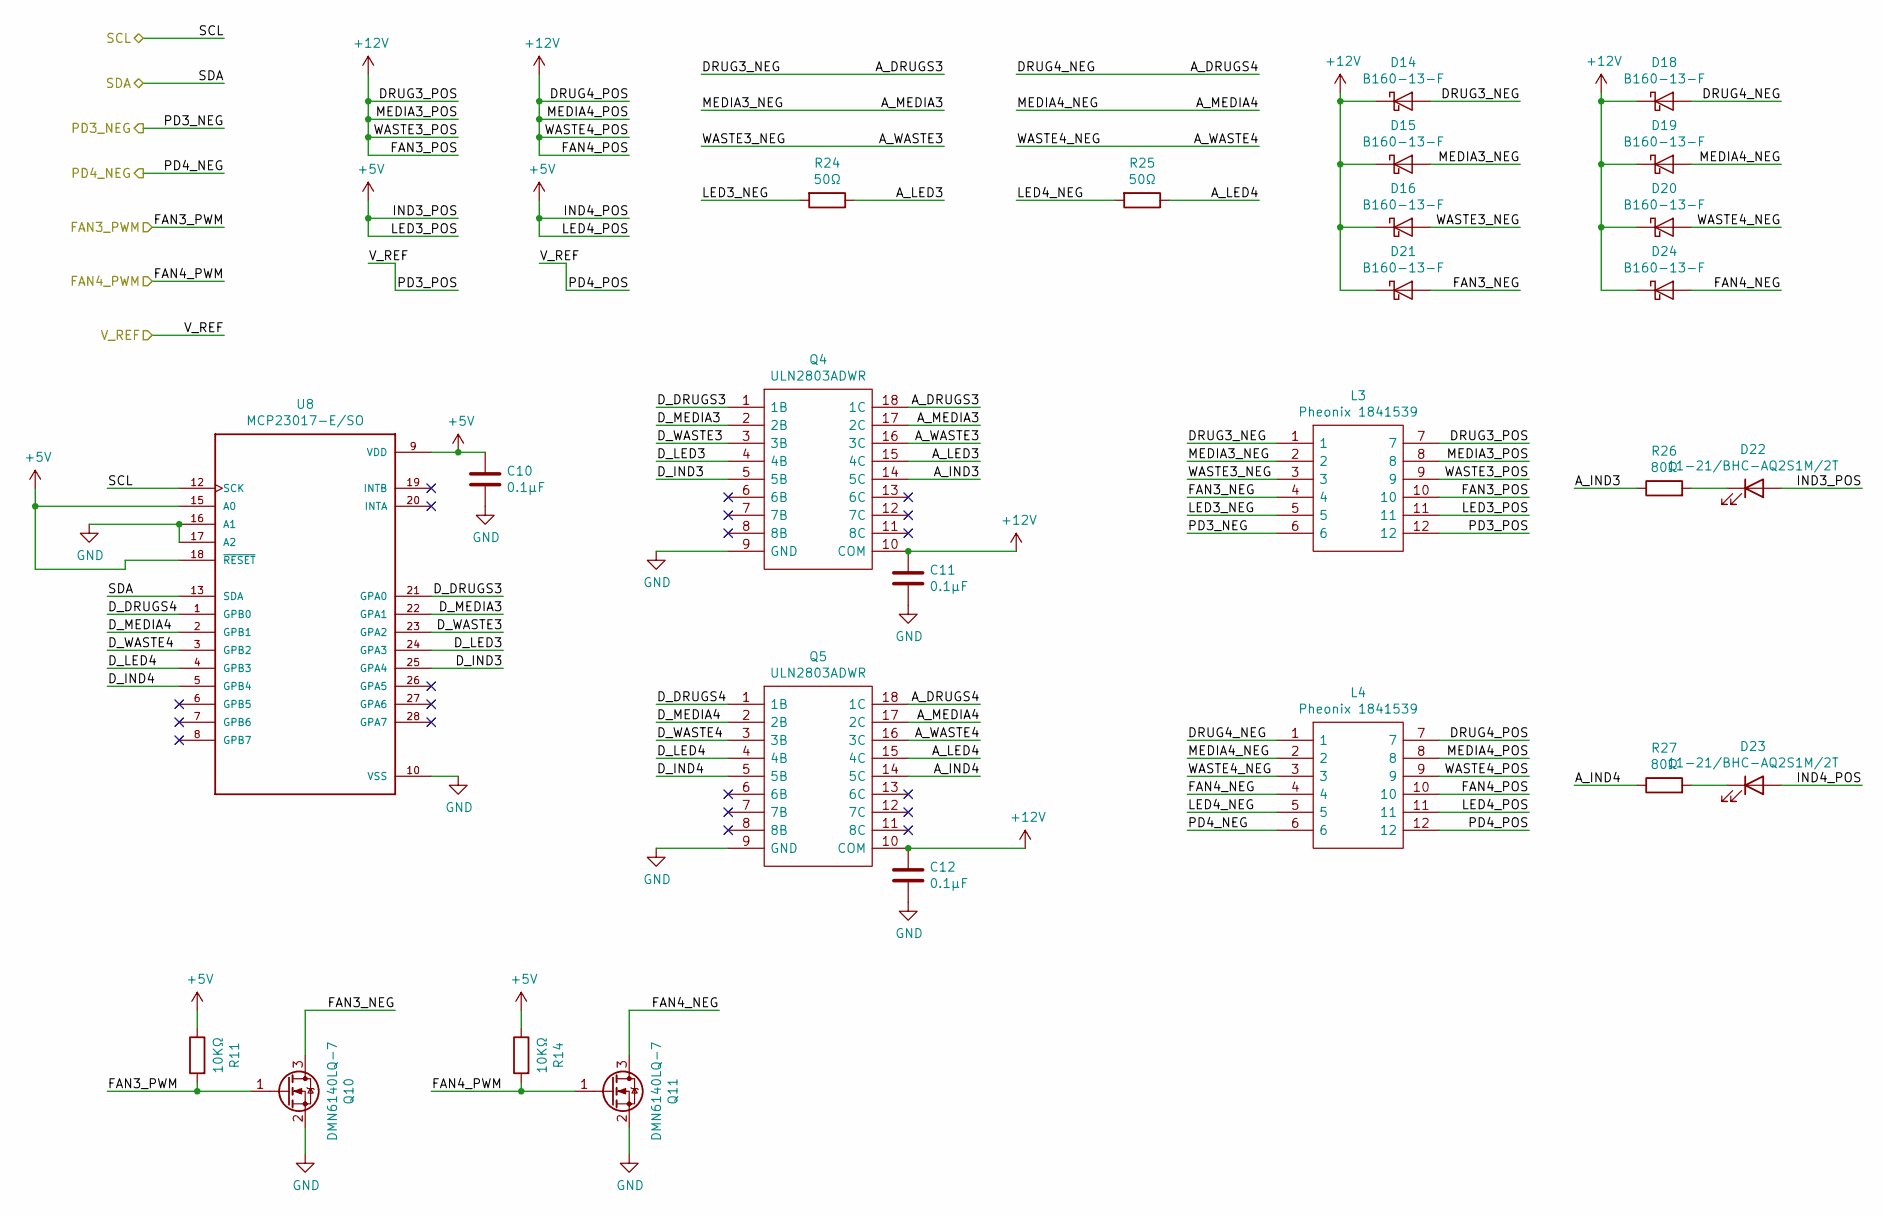
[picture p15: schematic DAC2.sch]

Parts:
C10, C11, C12: 0.1μF; C_0402_1005Metric; LCSC C1525
D14, D15, D16, D18, D19, D20, D21, D24: B160-13-F; D_SMA; LCSC C24784
D22, D23: 11-21/BHC-AQ2S1M/2T; LED_1206_3216Metric; LCSC C264323
L3, L4: Pheonix 1841539; 1841539; Mouser Part Number 651-1841539
Q4, Q5: ULN2803ADWR; SOIC-18W_7.5x11.6mm_P1.27mm; Mouser Part Number 595-ULN2803ADWR
Q10, Q11: DMN6140LQ-7; SOT-23; LCSC C155271
R11, R14: 10KΩ; R_0402_1005Metric; LCSC C25744
R24, R25: 50Ω; R_2512_6332Metric; LCSC C25487
R26, R27: 80Ω; R_0805_2012Metric; LCSC C17833
U8: MCP23017-E/SO; SOIC-28W_7.5x17.9mm_P1.27mm; LCSC C47023

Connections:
+5V: C10.1, D22.2 (A), D23.2 (A), L3.11, L4.11, R11.1, R14.1, U8.9 (VDD), U8.15 (A0), U8.18 (~RESET~); also elsewhere on the board
+12V: C11.1, C12.1, D14.1 (K), D15.1 (K), D16.1 (K), D18.1 (K), D19.1 (K), D20.1 (K), D21.1 (K), D24.1 (K), L3.7, L3.8, L3.9, L3.10, L4.7, L4.8, L4.9, L4.10, Q4.10 (COM), Q5.10 (COM); also elsewhere on the board
/DAC2/A_DRUGS3: D14.2 (A), L3.1, Q4.18 (1C)
/DAC2/A_DRUGS4: D18.2 (A), L4.1, Q5.18 (1C)
/DAC2/A_IND3: Q4.14 (5C), R26.1
/DAC2/A_IND4: Q5.14 (5C), R27.1
/DAC2/A_LED3: Q4.15 (4C), R24.1
/DAC2/A_LED4: Q5.15 (4C), R25.1
/DAC2/A_MEDIA3: D15.2 (A), L3.2, Q4.17 (2C)
/DAC2/A_MEDIA4: D19.2 (A), L4.2, Q5.17 (2C)
/DAC2/A_WASTE3: D16.2 (A), L3.3, Q4.16 (3C)
/DAC2/A_WASTE4: D20.2 (A), L4.3, Q5.16 (3C)
/DAC2/D_DRUGS3: Q4.1 (1B), U8.21 (GPA0)
/DAC2/D_DRUGS4: Q5.1 (1B), U8.1 (GPB0)
/DAC2/D_IND3: Q4.5 (5B), U8.25 (GPA4)
/DAC2/D_IND4: Q5.5 (5B), U8.5 (GPB4)
/DAC2/D_LED3: Q4.4 (4B), U8.24 (GPA3)
/DAC2/D_LED4: Q5.4 (4B), U8.4 (GPB3)
/DAC2/D_MEDIA3: Q4.2 (2B), U8.22 (GPA1)
/DAC2/D_MEDIA4: Q5.2 (2B), U8.2 (GPB1)
/DAC2/D_WASTE3: Q4.3 (3B), U8.23 (GPA2)
/DAC2/D_WASTE4: Q5.3 (3B), U8.3 (GPB2)
/DAC2/FAN3_NEG: D21.2 (A), L3.4, Q10.3 (D)
/DAC2/FAN4_NEG: D24.2 (A), L4.4, Q11.3 (D)
/DAC2/LED3_NEG: L3.5, R24.2
/DAC2/LED4_NEG: L4.5, R25.2
/FAN3_PWM: Q10.1 (G), R11.2; also elsewhere on the board
/FAN4_PWM: Q11.1 (G), R14.2; also elsewhere on the board
/PD3_NEG: L3.6; also elsewhere on the board
/PD4_NEG: L4.6; also elsewhere on the board
/SCL: U8.12 (SCK); also elsewhere on the board
/SDA: U8.13 (SDA); also elsewhere on the board
/V_REF: L3.12, L4.12; also elsewhere on the board
GND: C10.2, C11.2, C12.2, Q4.9 (GND), Q5.9 (GND), Q10.2 (S), Q11.2 (S), U8.10 (VSS), U8.16 (A1), U8.17 (A2); also elsewhere on the board
unnamed: D22.1 (K), R26.2
unnamed: D23.1 (K), R27.2

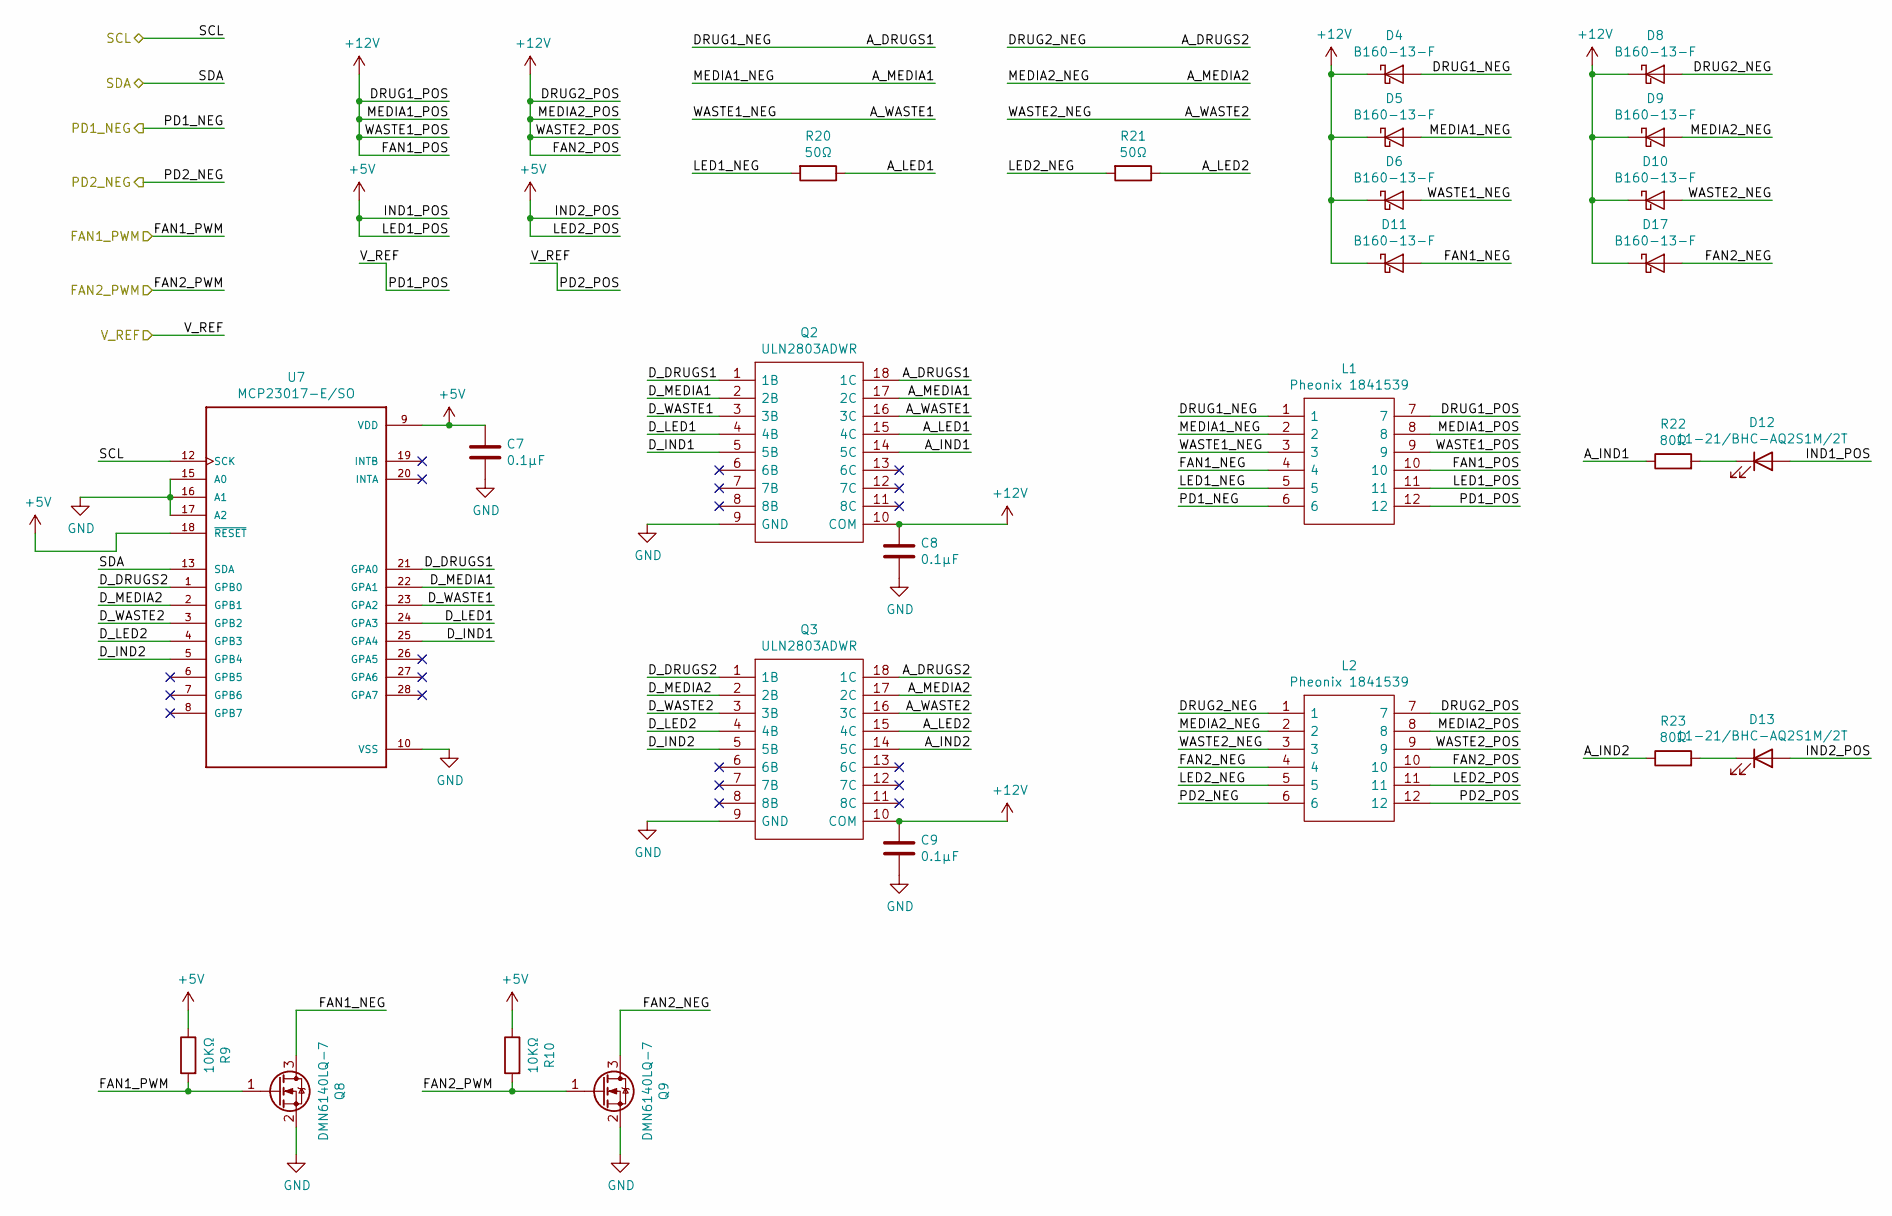
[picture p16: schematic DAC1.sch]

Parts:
C7, C8, C9: 0.1μF; C_0402_1005Metric; LCSC C1525
D4, D5, D6, D8, D9, D10, D11, D17: B160-13-F; D_SMA; LCSC C24784
D12, D13: 11-21/BHC-AQ2S1M/2T; LED_1206_3216Metric; LCSC C264323
L1, L2: Pheonix 1841539; 1841539; Mouser Part Number 651-1841539
Q2, Q3: ULN2803ADWR; SOIC-18W_7.5x11.6mm_P1.27mm; Mouser Part Number 595-ULN2803ADWR
Q8, Q9: DMN6140LQ-7; SOT-23; LCSC C155271
R9, R10: 10KΩ; R_0402_1005Metric; LCSC C25744
R20, R21: 50Ω; R_2512_6332Metric; LCSC C25487
R22, R23: 80Ω; R_0805_2012Metric; LCSC C17833
U7: MCP23017-E/SO; SOIC-28W_7.5x17.9mm_P1.27mm; LCSC C47023

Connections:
+5V: C7.1, D12.2 (A), D13.2 (A), L1.11, L2.11, R9.1, R10.1, U7.9 (VDD), U7.18 (~RESET~); also elsewhere on the board
+12V: C8.1, C9.1, D4.1 (K), D5.1 (K), D6.1 (K), D8.1 (K), D9.1 (K), D10.1 (K), D11.1 (K), D17.1 (K), L1.7, L1.8, L1.9, L1.10, L2.7, L2.8, L2.9, L2.10, Q2.10 (COM), Q3.10 (COM); also elsewhere on the board
/DAC1/A_DRUGS1: D4.2 (A), L1.1, Q2.18 (1C)
/DAC1/A_DRUGS2: D8.2 (A), L2.1, Q3.18 (1C)
/DAC1/A_IND1: Q2.14 (5C), R22.1
/DAC1/A_IND2: Q3.14 (5C), R23.1
/DAC1/A_LED1: Q2.15 (4C), R20.1
/DAC1/A_LED2: Q3.15 (4C), R21.1
/DAC1/A_MEDIA1: D5.2 (A), L1.2, Q2.17 (2C)
/DAC1/A_MEDIA2: D9.2 (A), L2.2, Q3.17 (2C)
/DAC1/A_WASTE1: D6.2 (A), L1.3, Q2.16 (3C)
/DAC1/A_WASTE2: D10.2 (A), L2.3, Q3.16 (3C)
/DAC1/D_DRUGS1: Q2.1 (1B), U7.21 (GPA0)
/DAC1/D_DRUGS2: Q3.1 (1B), U7.1 (GPB0)
/DAC1/D_IND1: Q2.5 (5B), U7.25 (GPA4)
/DAC1/D_IND2: Q3.5 (5B), U7.5 (GPB4)
/DAC1/D_LED1: Q2.4 (4B), U7.24 (GPA3)
/DAC1/D_LED2: Q3.4 (4B), U7.4 (GPB3)
/DAC1/D_MEDIA1: Q2.2 (2B), U7.22 (GPA1)
/DAC1/D_MEDIA2: Q3.2 (2B), U7.2 (GPB1)
/DAC1/D_WASTE1: Q2.3 (3B), U7.23 (GPA2)
/DAC1/D_WASTE2: Q3.3 (3B), U7.3 (GPB2)
/DAC1/FAN1_NEG: D11.2 (A), L1.4, Q8.3 (D)
/DAC1/FAN2_NEG: D17.2 (A), L2.4, Q9.3 (D)
/DAC1/LED1_NEG: L1.5, R20.2
/DAC1/LED2_NEG: L2.5, R21.2
/FAN1_PWM: Q8.1 (G), R9.2; also elsewhere on the board
/FAN2_PWM: Q9.1 (G), R10.2; also elsewhere on the board
/PD1_NEG: L1.6; also elsewhere on the board
/PD2_NEG: L2.6; also elsewhere on the board
/SCL: U7.12 (SCK); also elsewhere on the board
/SDA: U7.13 (SDA); also elsewhere on the board
/V_REF: L1.12, L2.12; also elsewhere on the board
GND: C7.2, C8.2, C9.2, Q2.9 (GND), Q3.9 (GND), Q8.2 (S), Q9.2 (S), U7.10 (VSS), U7.15 (A0), U7.16 (A1), U7.17 (A2); also elsewhere on the board
unnamed: D12.1 (K), R22.2
unnamed: D13.1 (K), R23.2

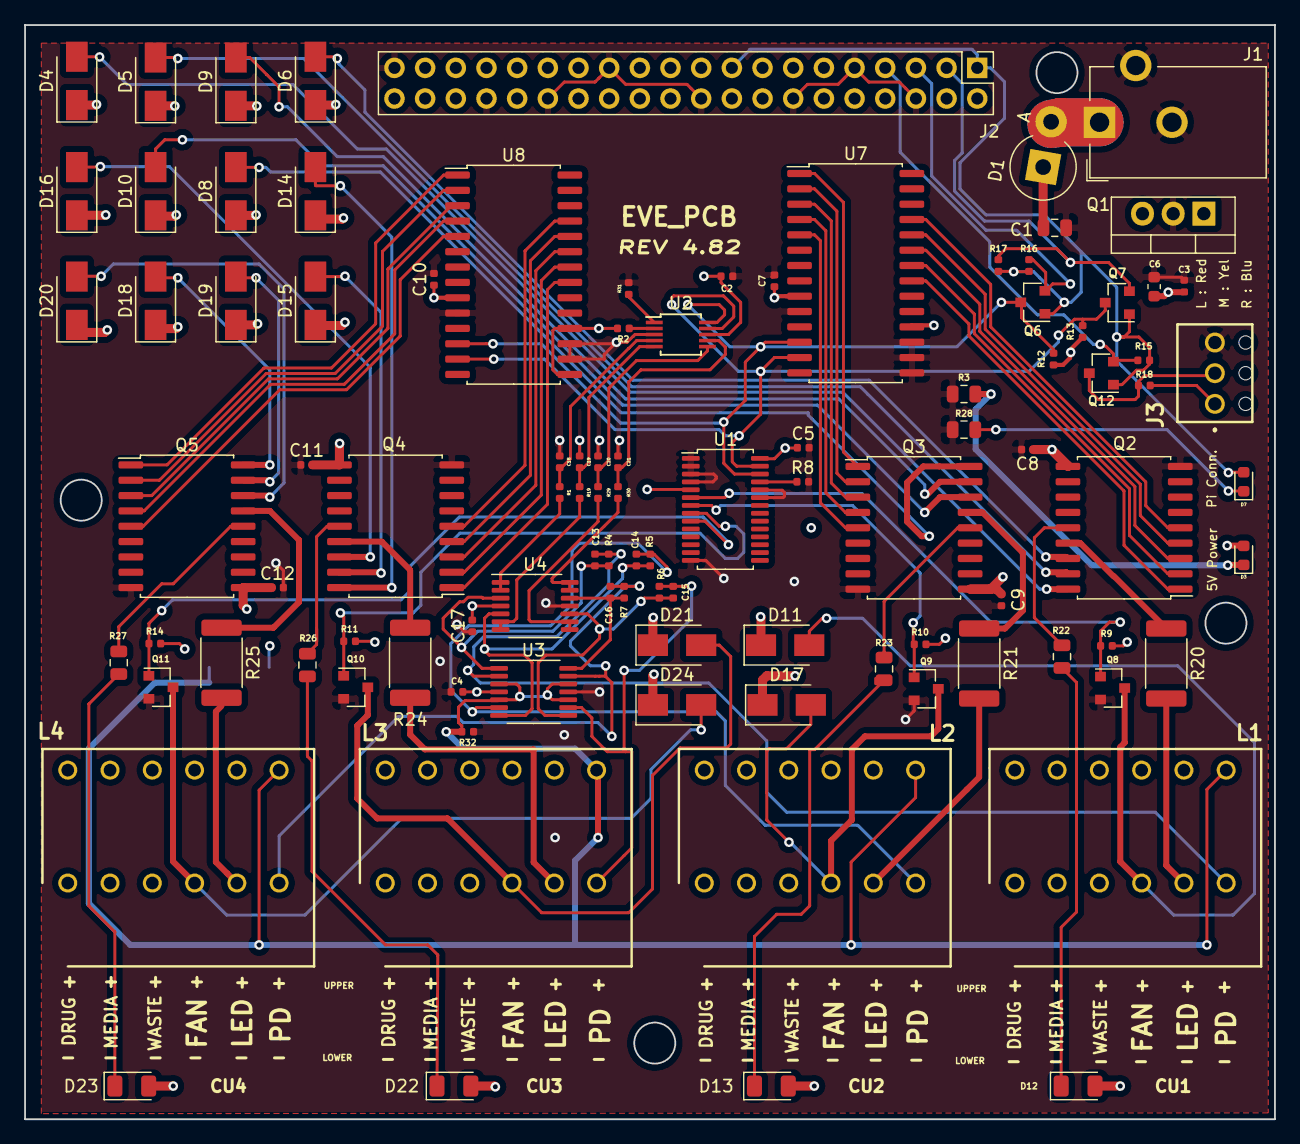
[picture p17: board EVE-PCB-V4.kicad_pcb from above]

Board: 4 copper layers, 103.5 x 90.6 mm, 102 parts (1 on the bottom side), 89 nets.

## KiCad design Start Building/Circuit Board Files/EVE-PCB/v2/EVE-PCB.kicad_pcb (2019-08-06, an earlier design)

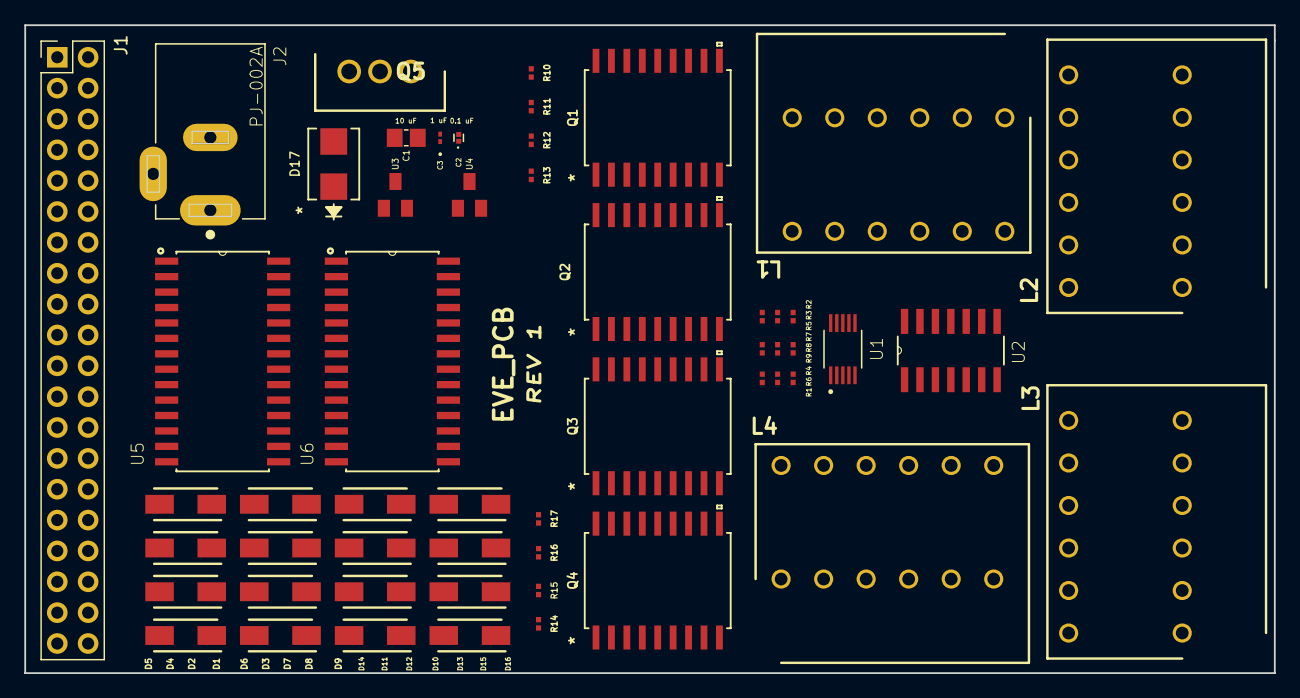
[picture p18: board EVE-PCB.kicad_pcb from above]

Board: 2 copper layers, 102.9 x 53.3 mm, 54 parts (0 on the bottom side), 70 nets, no tracks yet.

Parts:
C1: 10 uF; CAPC2012X135N
C2: 0.1 uF; CAPC0603X39N
C3: 1 uF; GRM033R71E102KA01D
D1, D2, D3, D4, D5, D6, D7, D8, D9, D10, D11, D12, D13, D14, D15, D16: BAT43; B160-13-F
D17: S1KB; S1KB-13-F
J1: Raspberry_Pi_2_3; PinHeader_2x20_P2.54mm_Vertical
J2: PJ-002A; CUI_PJ-002A
L1, L2, L3, L4: SHDR12W60P935X350_2X6_2250X1800X2420P; 1841539
Q1, Q2, Q3, Q4: DW18; ULN2803ADWR
Q5: TO254P465X1016X1883-3P; UA7805CKCT
R1, R2, R3, R4: 1M; RC0201FR-071ML
R5, R6, R7, R8, R9: 10K; RC0201FR-0710KL
R10, R12, R14, R16: 130; RC0201FR-07130RL
R11, R13, R15, R17: 400; RC0201FR-07402RL
U1: ADS1015IDGSR; SOP50P490X110-10N
U2: LM324DR; SOIC127P600X175-14N
U3, U4: BSN20BKR; BSN20_215
U5, U6: MCP23017T-E_SO; SOIC127P1030X265-28N

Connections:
+3V3: J1.1, J1.17, R5.1, R9.1, U3.1, U4.1
+5V: C2.1, C3.1, Q5.3, R6.2, R7.1, R8.2, U1.8, U2.4, U5.9, U5.18, U6.9, U6.18
+12V: C1.1, D1.1, D2.1, D3.1, D4.1, D5.1, D6.1, D7.1, D8.1, D9.1, D10.1, D11.1, D12.1, D13.1, D14.1, D15.1, D16.1, D17.1, L1.7, L1.8, L1.9, L1.10, L1.11, L2.7, L2.8, L2.9, L2.10, L2.11, L3.7, L3.8, L3.9, L3.10, L3.11, L4.7, L4.8, L4.9, L4.10, L4.11, Q1.10, Q2.10, Q3.10, Q4.10, Q5.1
/AIN0: R1.1, U1.4, U2.1
/AIN1: R2.1, U1.5, U2.7
/AIN2: R3.1, U1.6, U2.8
/AIN3: R4.1, U1.7, U2.14
/DAC1/A_DRUGS1: D1.2, L1.1, Q1.18
/DAC1/A_DRUGS2: D5.2, L2.1, Q2.18
/DAC1/A_FAN1: Q1.14, R11.1
/DAC1/A_FAN2: Q2.14, R13.1
/DAC1/A_LED1: Q1.15, R10.1
/DAC1/A_LED2: Q2.15, R12.1
/DAC1/A_MEDIA1: D2.2, L1.2, Q1.17
/DAC1/A_MEDIA2: D6.2, L2.2, Q2.17
/DAC1/A_SFAN1: D4.2, L1.4, Q1.13, R11.2
/DAC1/A_SFAN2: D8.2, L2.4, Q2.13, R13.2
/DAC1/A_WASTE1: D3.2, L1.3, Q1.16
/DAC1/A_WASTE2: D7.2, L2.3, Q2.16
/DAC1/D_DRUGS1: Q1.1, U5.21
/DAC1/D_DRUGS2: Q2.1, U5.1
/DAC1/D_FAN1: Q1.5, U5.25
/DAC1/D_FAN2: Q2.5, U5.5
/DAC1/D_LED1: Q1.4, U5.24
/DAC1/D_LED2: Q2.4, U5.4
/DAC1/D_MEDIA1: Q1.2, U5.22
/DAC1/D_MEDIA2: Q2.2, U5.2
/DAC1/D_SFAN1: Q1.6, U5.26
/DAC1/D_SFAN2: Q2.6, U5.6
/DAC1/D_WASTE1: Q1.3, U5.23
/DAC1/D_WASTE2: Q2.3, U5.3
/DAC1/LED1_NEG: L1.5, R10.2
/DAC1/LED2_NEG: L2.5, R12.2
/DAC2/A_DRUGS3: D9.2, L3.1, Q3.18
/DAC2/A_DRUGS4: D13.2, L4.1, Q4.18
/DAC2/A_FAN3: Q3.14, R15.1
/DAC2/A_FAN4: Q4.14, R17.1
/DAC2/A_LED3: Q3.15, R14.1
/DAC2/A_LED4: Q4.15, R16.1
/DAC2/A_MEDIA3: D10.2, L3.2, Q3.17
/DAC2/A_MEDIA4: D14.2, L4.2, Q4.17
/DAC2/A_SFAN3: D12.2, L3.4, Q3.13, R15.2
/DAC2/A_SFAN4: D16.2, L4.4, Q4.13, R17.2
/DAC2/A_WASTE3: D11.2, L3.3, Q3.16
/DAC2/A_WASTE4: D15.2, L4.3, Q4.16
/DAC2/D_DRUGS3: Q3.1, U6.21
/DAC2/D_DRUGS4: Q4.1, U6.1
/DAC2/D_FAN3: Q3.5, U6.25
/DAC2/D_FAN4: Q4.5, U6.5
/DAC2/D_LED3: Q3.4, U6.24
/DAC2/D_LED4: Q4.4, U6.4
/DAC2/D_MEDIA3: Q3.2, U6.22
/DAC2/D_MEDIA4: Q4.2, U6.2
/DAC2/D_SFAN3: Q3.6, U6.26
/DAC2/D_SFAN4: Q4.6, U6.6
/DAC2/D_WASTE3: Q3.3, U6.23
/DAC2/D_WASTE4: Q4.3, U6.3
/DAC2/LED3_NEG: L3.5, R14.2
/DAC2/LED4_NEG: L4.5, R16.2
/PD1_NEG: L1.6, R1.2, U2.2
/PD2_NEG: L2.6, R2.2, U2.6
/PD3_NEG: L3.6, R3.2, U2.9
/PD4_NEG: L4.6, R4.2, U2.13
/SCL: R6.1, U1.10, U3.3, U5.12, U6.12
/SCL-3.3: J1.5, R5.2, U3.2
/SDA: R8.1, U1.9, U4.3, U5.13, U6.13
/SDA-3.3: J1.3, R9.2, U4.2
GND: C1.2, C2.2, C3.2, J1.6, J1.9, J1.14, J1.20, J1.25, J1.30, J1.34, J1.39, J2.2, J2.3, L1.12, L2.12, L3.12, L4.12, Q1.9, Q2.9, Q3.9, Q4.9, Q5.2, U1.1, U1.3, U2.3, U2.5, U2.10, U2.11, U2.12, U5.10, U5.15, U5.16, U5.17, U6.10, U6.15, U6.16, U6.17
unnamed: D17.2, J2.1
unnamed: R7.2, U1.2

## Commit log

2019-06-19 added sample configuration file
2019-07-18 Added temperature sensing
2019-08-05 Added 3D files
    [Base.SLDPRT, Base.stl, Cap.SLDPRT, Cap.stl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]
2019-08-06 Added Circuit Board files
    [DAC and Outputs.sch, DAC1.sch, DAC2.sch, EVE-PCB-V2.dsn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]
2019-08-08 Added Parts List
    [Parts List.xlsx]
2019-09-16 Update Parts List
    [Parts List.xlsx, PartsList.xlsx]
2019-09-21 Seperate flow rates
    [Configuration File Parameter Definitions.xlsx]
2020-04-20 PCB Updates
    [DAC1.sch, DAC2.sch, EVE-PCB-V2.kicad_pcb, EVE-PCB.sch]
2020-05-22 PCB v4.5 and below
    [DAC and Outputs.sch, DAC1.sch, DAC2.sch, EVE-PCB-V2-B_Cu.gbr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]
2020-05-23 PCB v4.5 temp sensor PCB addition
    [EVE-PCB-V4.kicad_pcb, EVE-PCB-V4.sch]
2020-05-29 Updates to v4.5 and include support for ADS1115
    [BOM.csv, CPL.csv, EVE-PCB-V4-B_Cu.gbr, EVE-PCB-V4-B_Mask.gbr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]
2020-06-10 v4.5 updates
    [EVE-PCB-V4-B_Cu.gbr, EVE-PCB-V4-B_Mask.gbr, EVE-PCB-V4-B_Paste.gbr, EVE-PCB-V4-B_SilkS.gbr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]
2020-06-11 Update configuration paramater definitions
    [Configuration File Parameter Definitions.xlsx]
2020-06-12 Update pumpsledoff.py to include optional indicator LEDs
2020-06-13 Add indicator light support to LED test script
2020-06-18 Bump PCB version to 4.81
    - Added buffer before ADC
    - Reduced photodiode amplification to limit saturation
    - Added optional 1V Vref to TIA
    - Added passive 50Hz low pass filter before ADC
    [BOM.csv, DAC1.sch, DAC2.sch, EVE-PCB-V4-B_Cu.gbr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]
2020-06-19 Update schematic pdf
    [EVE-PCB-V4.kicad_pcb, EVE-PCB-V4.sch]
2020-06-26 Bump PCB version to 4.81
    - Fixed voltages for fan and LED
    [DAC1.sch, DAC2.sch, EVE-PCB-V4-B_Cu.gbr, EVE-PCB-V4-B_Mask.gbr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]
2020-07-15 Updates to PCB 4.81
    [BOM.csv, Base.SLDPRT, Base.stl, Cap.SLDPRT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]
2020-07-16 Implement software low-pass filter for OD readings
2020-07-16 Fixes for software low-pass filter
2020-07-22 Update 3D Files
    [Cap.STL, Cap.stl, Holder.STL, Holder.stl]
2020-07-28 Bump PCB to version 4.82
    - Update schematic to use V_ref as PD positive terminal.
    - Update PCB to allow for this change.
    [DAC1.sch, DAC2.sch, EVE-PCB-V4-B_Cu.gbr, EVE-PCB-V4-B_Mask.gbr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]
2020-07-30 Update circuit schematic
2020-11-20 Add PCB image
2020-11-20 Add PCB and Holder image
